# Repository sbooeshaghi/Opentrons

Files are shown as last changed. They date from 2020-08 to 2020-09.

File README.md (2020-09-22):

# Opentrons OT-1 Lab robot

## Intro and repository structure
This repository is aimed to be a guide for working with the OT-1 lab robot.

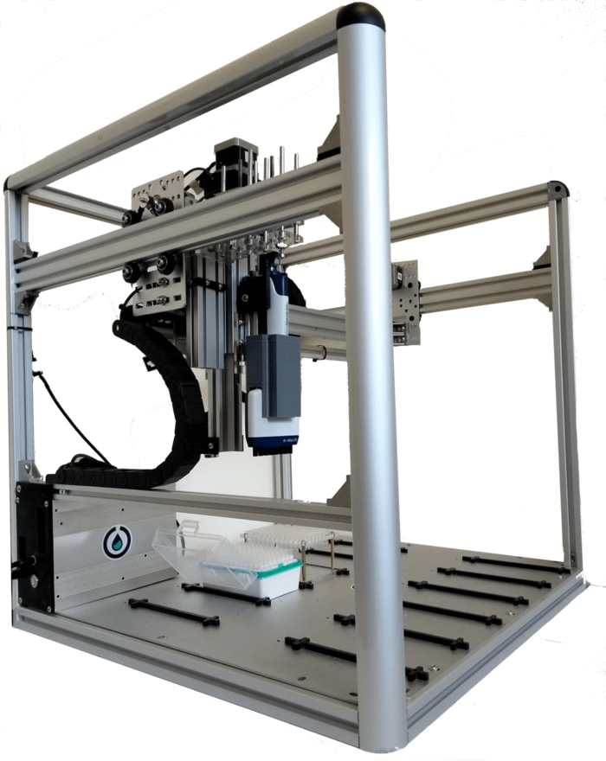
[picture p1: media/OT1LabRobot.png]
 *The OT-1 Lab robot*

The structure of the repository is as follows:
```
HARDWARE/
|
|--> drawings/
|--> stl files/
SOFTWARE/
|
|--> protocols/
media/
README.md
```
This README file explains how to set up the robot, how to create a protocol, how to calibrate the robot and finally how to run the protocol on the robot. The repository furthermore contains 3 folders with additional documentation: The `HARDWARE` folder contains technical drawings of the robot. Furthermore, some stl files and drawings are dedicated to *firm labware attachment* which is indispensible for good calibration. The `SOFTWARE` folder contains example protocols, accompanied with diagrams to explain them. Additionaly, a python notebook is included to illustrate how to create a protocol with jupyter notebooks. Finally, the `media` folder contains pictures and gifs used for this README file. 

## Contents
In this section, a quick overview of what follows is given:

1. Connect robot and open the OT-1 app
    - Connect robot
    - Open/download the app
    - Move the robot
1. Write the protocol
    - Test the protocol code in jupyter notebooks
    - Create the protocol script
1. Upload, calibrate and run
    - Upload the protocol in the app
    - Attach the labware to the robot
    - Calibrate the labware
    - Run the protocol

## 1. Connect robot and open the OT-1 app
### Connect robot
Plug the power cable into the power outlet and the usb cable into your laptop. Then press the power button.

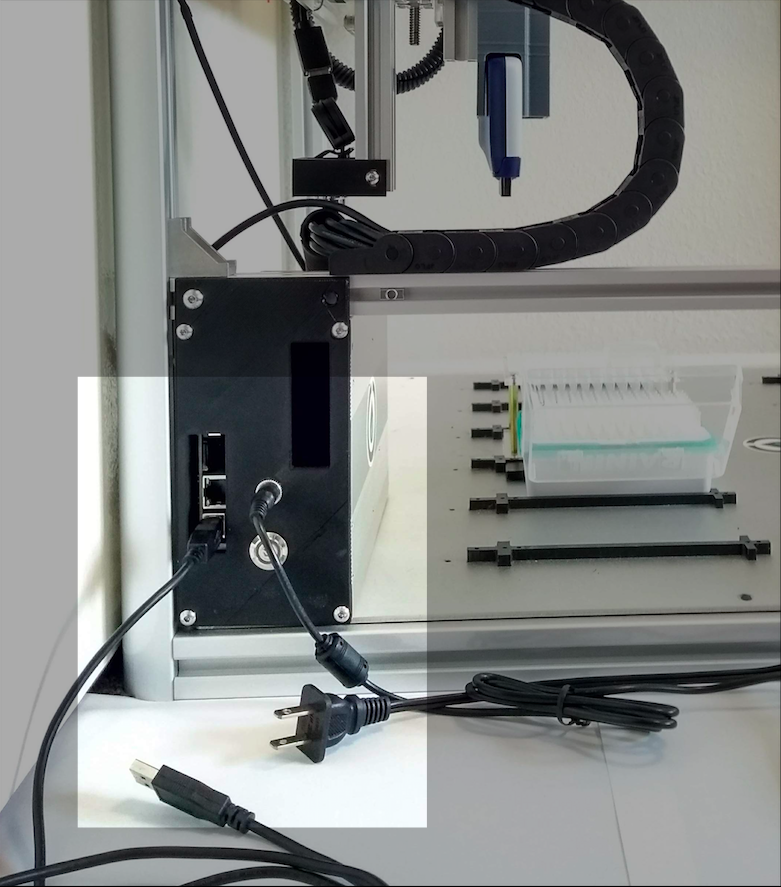
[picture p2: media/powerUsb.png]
 *Connect to the power outlet and plug the usb cable in your laptop. Press the power button.*

### Open/download the OT-1 app
Open the Opentrons 1 App. If you don't have it downloaded yet, download the app from the [opentrons site](https://opentrons.com/ot-app/). *Remark: Make sure you download the OT-1 and not the OT-2 app.(OT-1 is in fact the prototype of OT-2. So most documentation you find on the opentrons website is on OT-2.)* 
When you open the app you get a screen that looks like this:
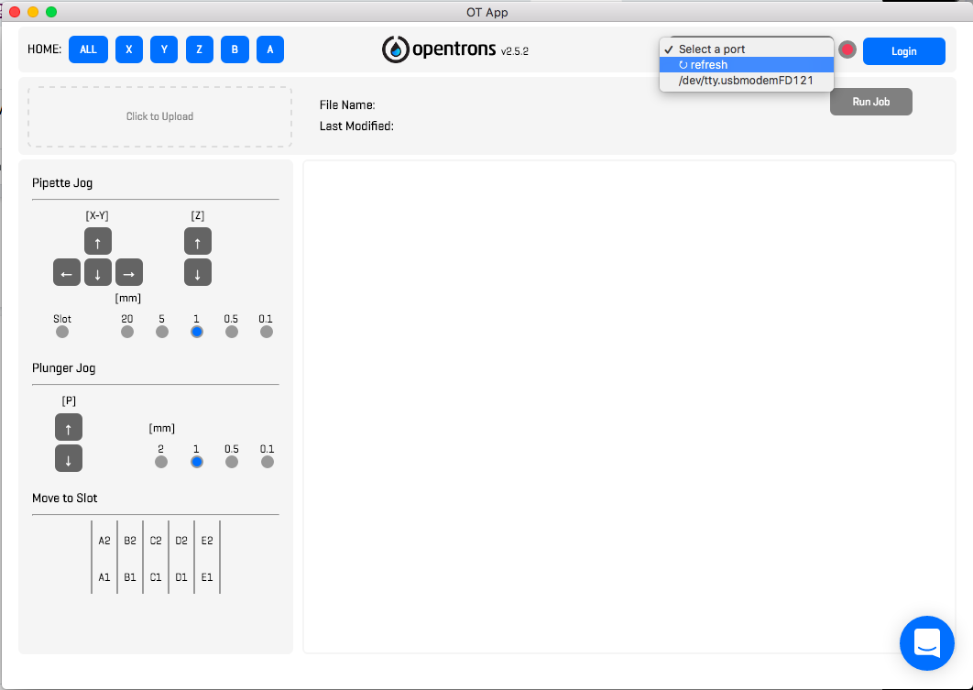
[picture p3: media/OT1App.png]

*The layout of the OT-1 App.*

You want to select the port that has a name similar to:
  */dev/tty.usbmodemFD121*
Then the app will suggest to home the robot. If you press ok, the robot will move to its home position.

### Move the robot
If all went well, you can now play with the buttons and move the robot around. X,Y and Z coordinates are controlled through the Pipette Jog buttons. The Plunger Jog buttons are responsible for moving the pipette plunger following a system as shown in gif below:

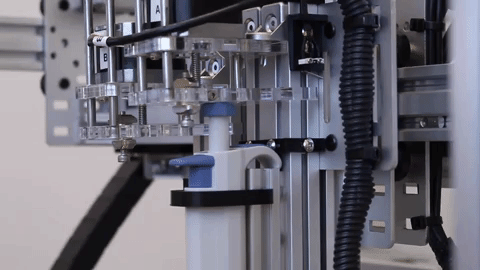
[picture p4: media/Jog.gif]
 *Controlling the plunger.*

## 2. Write the protocol
Protocols are used to pass on subsequent steps that make up a certain experiment to the robot. 
We will consider a simple test code which uses an 8-channel 200 µl pipette to transfer 100 µl of liquid from the first to the second row of a 200 µl 96-wells plate.

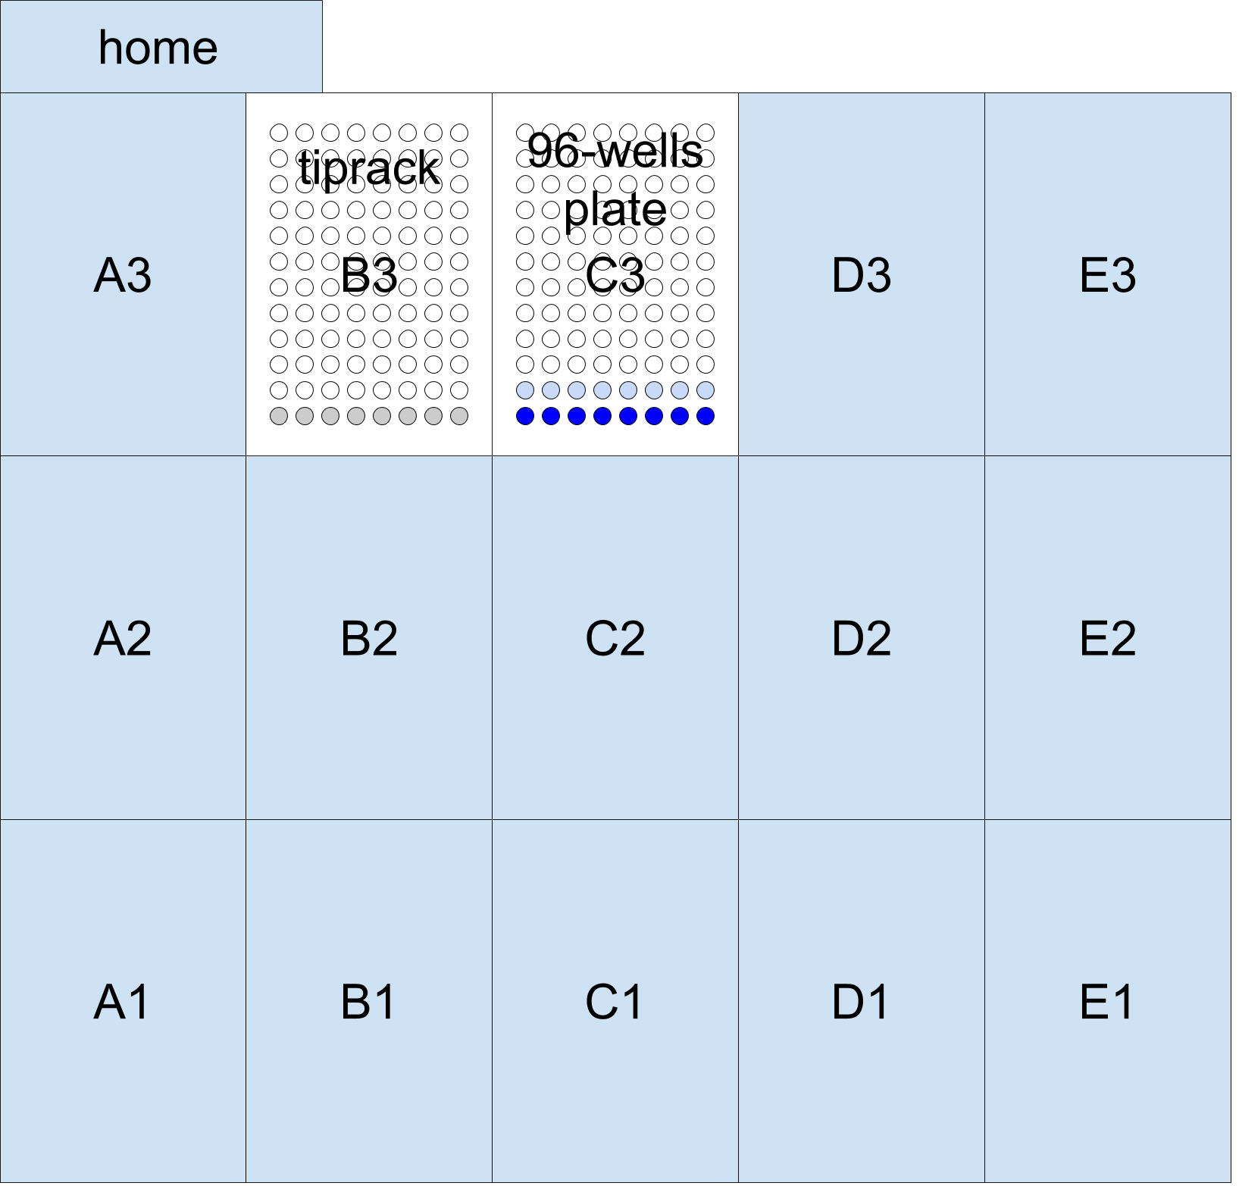
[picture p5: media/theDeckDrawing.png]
*Illustration of the example protocol*

~~~

## Use the Opentrons API's containers and instruments
from opentrons import containers, instruments

## PART I: Add containers and pipettes:
# containers:
# Add a 96 well plate of 20 mm deep, and place it in slot 'C3'
plate = containers.load('96-well-plate-20mm', 'C3', 'plate')
# Add a 200uL tip rack, and place it in slot 'B3'
tiprack = containers.load('tiprack-200ul', 'B3','tiprack')

# pipettes:
# Add a 200uL 8 channel pipette to axis 'a', and tell it to use that tip rack
pipette = instruments.Pipette(
    axis='a',
    channels=8,
    max_volume=200, tip_racks=[tiprack])

## PART II: Specify protocol
# commands:
# Transfer 100uL from the plate's first row of wells to it's second row of wells.
pipette.transfer(100, plate.rows[0], plate.rows[1])

~~~

*Code of the example protocol*

The code above already contains the most important commands and the typical structure of a protocol:
* Part I: 
    * Adding the containers
    * Adding the pipette(s)
* Part II: Specifying the commands

A good overview of the opentrons API (for OT1) can be found [here](https://docs.opentrons.com/ot1/index.html). Taking a look at these pages is probably the easiest method to go a long way in writing protocols.

*Remark: When adding a container it is important to choose a container that has the exact right dimensions to avoid collisions with the robot. E.g. The '96-well-plate-20mm' is well specified because ‘96-well’ plates have standard well positions and the depth is in this case 20 mm. The dimensions of this plate correspond exactly to the dimensions of the physical plate used in the example.  A list of the most common built in containers can be found [here](https://docs.opentrons.com/ot1/containers.html#labware-library). It is also possible to make your own custom containers.* 

### Test the protocol code in jupyter notebooks

To make sure you are using correct commands when writing the code, it is a good idea to use the opentrons python package and testrun the code in e.g. jupyter notebooks to see if you get any errors (the robot won’t work, but you can at least see if the code runs).

To install the package run:
~~~
>> pip install opentrons==2.5.2
~~~
in the terminal (this is the OT-1 version).

While testing the protocol you can now add some print statements to get additional feedback on the code. A useful tool is the robot package from which you can print the robot commands. 

<pre>

<b>from opentrons import robot
robot.clear_commands()</b>

## Use the Opentrons API's containers and instruments
from opentrons import containers, instruments

## PART I: Add containers and pipettes:
# containers:
# Add a 96 well plate of 20 mm deep, and place it in slot 'C3'
plate = containers.load('96-well-plate-20mm', 'C3', 'plate')
# Add a 200uL tip rack, and place it in slot 'B3'
tiprack = containers.load('tiprack-200ul', 'B3','tiprack')

<b> print(plate,tiprack) </b>

# pipettes:
# Add a 200uL 8 channel pipette to axis 'a', and tell it to use that tip rack
pipette = instruments.Pipette(
    axis='a',
    channels=8,
    max_volume=200, tip_racks=[tiprack])
<b> print(pipette.max_volume)  </b>   
    
## PART II: Specify protocol
# commands:
# Transfer 100uL from the plate's first row of wells to it's second row of wells.
pipette.transfer(100, plate.rows[0], plate.rows[1])

<b> for c in robot.commands():
    print(c) </b>
</pre>
*Code of the example protocol with additional print statements (in bold)*

These print statements can be removed in the eventual protocol (the robot just ignores them when running the protocol) but are a good first check of your code.  For this code the output becomes:

~~~
<Container plate> <Container tiprack>
200
Picking up tip from <WellSeries: <Well A1><Well B1><Well C1><Well D1><Well E1><Well F1><Well G1><Well H1>>
Aspirating 100.0 at <WellSeries: <Well A1><Well B1><Well C1><Well D1><Well E1><Well F1><Well G1><Well H1>>
Dispensing 100.0 at <WellSeries: <Well A2><Well B2><Well C2><Well D2><Well E2><Well F2><Well G2><Well H2>>
Returning tip
Drop_tip at <WellSeries: <Well A1><Well B1><Well C1><Well D1><Well E1><Well F1><Well G1><Well H1>>
~~~
*Output of code with additional print statements using jupyter notebooks*

*Remark: As an alternative to this explanation, the folder `SOFTWARE/protocols/` contains a python notebook to explain the creation of protocols with jupyter notebooks more interactively.*

### Create the protocol script
Once your protocol runs as expected on jupyter notebooks, you make it into a python script. (Simply paste it into a plain text document and add .py extension). This example protocol has been uploaded in the folder `SOFTWARE/protocols/`.

## 3. Upload, calibrate and run
### Upload the protocol in the app
In the OT-1 app you can now select the ‘Click to Upload’ button and upload your script to the app. 

### Attach the labware to the robot
Before we can calibrate, we must place the containers and attach the pipette. In this case, a [Rainin 200 µl, 8 channel pipette](https://www.mt.com/us/en/home/products/pipettes/manual-pipettes/multichannel-pipettes.html) was used. To make sure the pipette is attached rigidly, a 3D printed holder was made (stl file in the `HARDWARE/stl files/` folder). The tiprack and 96-wells plate are also placed in such a way that they can not move. Documentation on the topic of efficiently placing labware is located in `HARDWARE/`. A rigid placement of the labware will save a of time calibrating.

*Remark: The robot only knows about the instruments and containers declared in your script. To prevent collisions, no unexpected objects should be on the deck.*

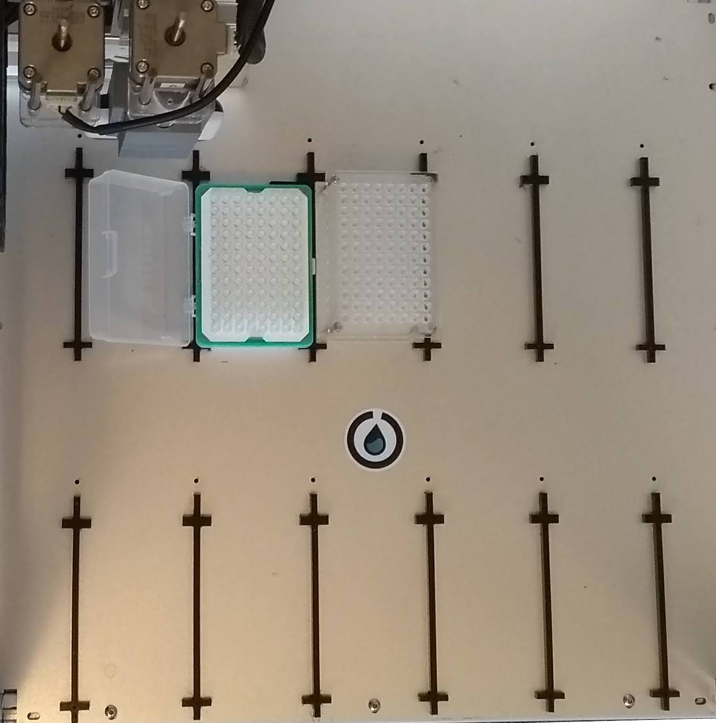
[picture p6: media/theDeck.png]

*the OT-1 robot with the containers and pipette on the right positions*

### Calibrate the labware
Once the protocol has been uploaded, the app will identify the instruments used in the script and provide you with an interface to calibrate them. For this example, you’ll have to calibrate the pipettes top, bottom, blowout and drop plunger positions and the positions of the tiprack and the 96 wells plate. Of course this can only be done after attaching the pipette and placing the tiprack and 96-wells plate on the deck of the robot.
#### Pipette calibration
For the pipette, we need to calibrate the plunger positions and set the volume range such that the robot has all the information to handle the pipette. *Remark: some dry but useful explanation on handling pipettes for novices can be found [here](https://www.youtube.com/watch?v=QGX490kuKjg).*

Opentrons explains pipette calibration quite well on this [webpage](https://support.opentrons.com/en/articles/689990-calibrating-the-pipettes). However, I do have the following remarks:
- I think the description for calibrating the pipettes top and bottom positions is good:
    - Top: plunger is positioned almost all the way up (but still being pressed down just a tiny bit)
    - Bottom: plunger is at or slightly above its “first-stop” or “soft-stop”

    However, I would change the descriptions to set blow out and drop positions:
    - Blow Out:  <s> plunger is all the way down to it's “second-stop” or “hard-stop”, making sure any attached tip do not get pushed off </s>. plunger at the same position as bottom.
    - Drop Tip: Forces any attached tip to fall off. This should coincide with the plunger being all the way down to its “second-stop” or “hard-stop. 

    The reason for these adjustments is that if you make ‘Blow Out’ coincide with the hard stop, any further movement of the motor will press the whole pipette down and it will cause strain and bending to the pipette and connecting parts. Note that since ‘Blow Out’ and ‘Bottom’ are now at the same position, there is no real blow out functionality anymore. *Remark: This makes sense because there is only one motor (read: 1 degree of freedom) pressing down both the plunger and the ejector button. This shouldn't pose a big problem, to aspirate and dispense a specified amount of liquid, knowledge of top and bottom position is sufficient. Traditionally, blow out is used to remove as much as possible of the remaining liquid in the tips (which normally is very little). When it is critical that the tips are completely clean we can drop them and pick up a new set.*
- Related to the previous remark: To make sure the ‘Drop Tip’ position will coincide with the hard stop it is important to adjust the ejector screw such that it will press the ejector button hard enough for the tips to drop when the plunger is at the hard stop.
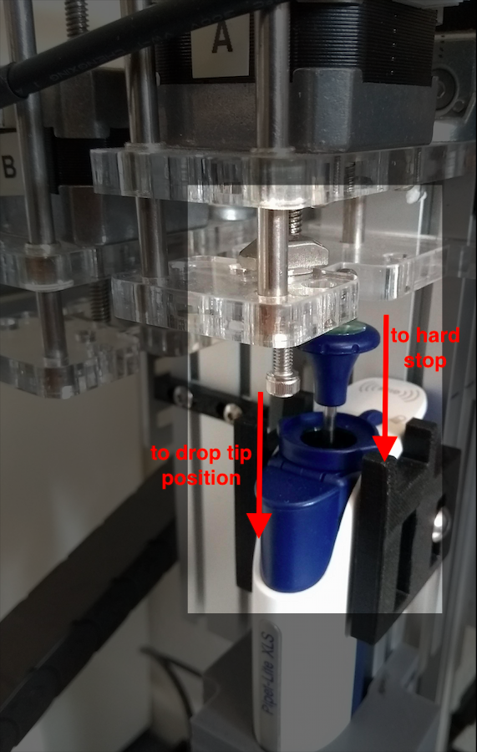
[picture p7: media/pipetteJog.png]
     *When the plunger moves to hard stop position, the screw simultaneously pushes the ejector button to reach ‘drop tip’ position.*

#### Container calibration
The containers have now been placed on the robot deck. The dimensions of the containers are known and specified in the script. Now the only thing that remains is to determine their exact position. The position has to be specified perfectly to avoid collisions. This is done in the calibration process. 

Opentrons explains calibration of containers very well on this [webpage](https://support.opentrons.com/en/articles/689977-calibrating-the-deck).

### Run the protocol
Press the Run Job button in the Opentrons App.
([video](https://drive.google.com/file/d/1IdHP-5DXYBkbdMaAbL4stZ4RvGIAhJ0E/view?usp=sharing): best adjust the quality to 1080p.)

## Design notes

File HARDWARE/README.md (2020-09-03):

## HARDWARE

The `HARDWARE` folder is mainly focussed on the firm attachment of labware to the robot which is required for a good calibration and therefore indispensible for efficient work with the robot.
There are 2 subfolders:
* `drawings`: In this folder some technical drawings of the robot-deck and common containers are included. The drawings are presented in md-files and linked to a google drawing with the right dimensions. Furthermore, 2 possible designs for labware to deck attachment are presented.
* `stl files`: This folder contains stl files for the 3D printing of additional pieces to attach labware firmly to the robot.

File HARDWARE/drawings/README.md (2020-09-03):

## Drawings
In this folder some technical drawings are included. The drawings are presented in md-files and linked to a google drawing. By clicking on the drawing you get referred to the original google drawing which is drawn in the right dimensions.

* `Slots.md` contains a representation of the robot deck
* `96 wells.md` is a drawing of a 96 wells plate

Furthermore, this folder contains 2 subfolders which represent suggested designs for labware to deck attachment. *I made these designs because I wanted to optimize the immobility of the labware which is critical for a good calibration and therefore indispensible for efficient work with the labrobot in general.*

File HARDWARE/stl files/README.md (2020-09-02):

## Stl files

This folder contains the following stl files:

1. `pipetteholderv5.stl` : a prop to attach the pipette rigidly to the opentrons labrobot
1. `tiprackfixerv3.stl` : a prop to fix the tiprack rigidly to the opentrons labrobot

Furthermore, this folder contains some images to illustrate their working.

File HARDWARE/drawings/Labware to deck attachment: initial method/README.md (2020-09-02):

## Labware to deck attachment: initial method

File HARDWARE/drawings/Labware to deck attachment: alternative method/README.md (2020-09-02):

## Labware to deck attachment: alternative method
(by adding acrylic baseplate)

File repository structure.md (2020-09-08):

```
HARDWARE/
|
|--> drawings/
     |
     |--> Labware to deck attachment: alternative method/
          |
          |--> Acrylic deck design.md
          |--> Acrylic plate designs for labware attachment.md
          |--> README.md
     |--> Labware to deck attachment: initial method/
          |
          |--> 3D printed option for tiprack attachment.md
          |--> Acrylic plate designs for labware attachment.md
          |--> README.md
     |--> 96 wells.md
     |--> README.md
     |--> Slots.md
|--> stl files/
     |
     |--> README.md
     |--> pipetteholderv5.stl
     |--> tiprackfixerv3.stl
|--> README.md
SOFTWARE/
|
|--> protocols/
     |
     |--> Diagram: Example protocol.md
     |--> Diagram: Refill protocol.md
     |--> Diagram: Split pool barcoding protocol.md
     |--> README.md
     |--> Split pool barcoding protocol.ipynb
     |--> Split pool barcoding protocol.py
     |--> example_protocol.py
     |--> refill_protocol.py
|--> README.md
media/
|
|--> Jog.gif
|--> OT1App.png
|--> ...
|--> README.md
README.md
```

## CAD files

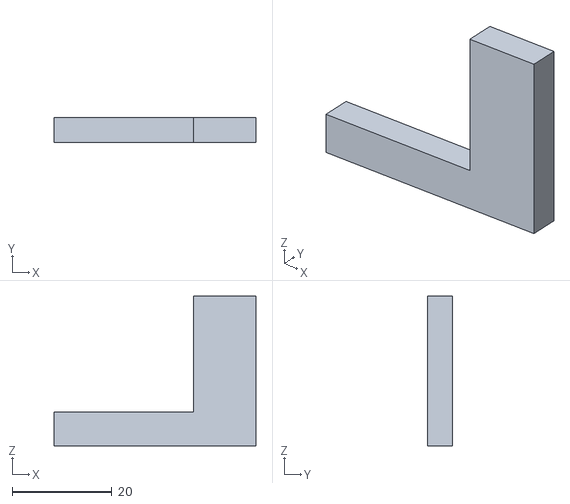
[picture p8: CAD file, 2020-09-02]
HARDWARE/stl files/tiprackfixerv3.stl
40.5 x 5.00 x 30.0

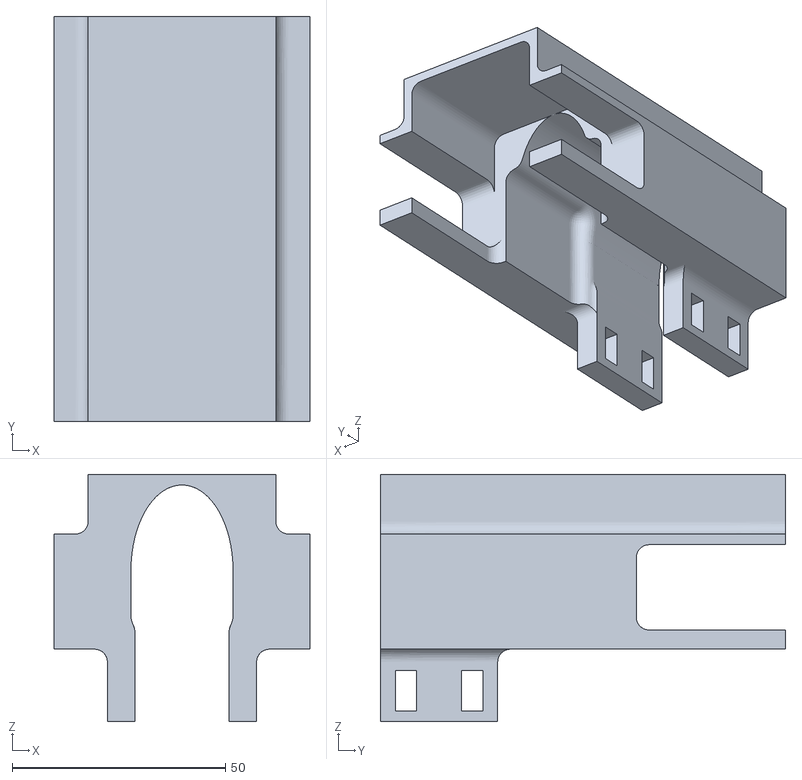
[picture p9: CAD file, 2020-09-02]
HARDWARE/stl files/pipetteholderv5.stl
60.0 x 95.0 x 58.0

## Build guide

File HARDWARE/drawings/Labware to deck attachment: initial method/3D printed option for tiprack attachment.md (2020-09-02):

[](https://docs.google.com/drawings/d/1fZovzV_FYyxDqWP138ZGucMIR-l8z0wgo1t7G0zVV-k/edit)

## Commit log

2020-09-02 Update and rename HARDWARE/drawings/Labware to deck attachment: Option 2 (add acrylic base plate)/README.md to HARDWARE/drawings/Labware to deck attachment: alternative method/README.md
    https://stackoverflow.com/questions/31861651/how-to-rename-a-directory-folder-on-github-website
2020-09-02 Create Labware to deck attachment: initial method
2020-09-02 Create 3D printed option for tiprack attachment.md
2020-09-02 Update 3D printed option for tiprack attachment.md
2020-09-02 Create Acrylic plate designs for labware attachment.md
